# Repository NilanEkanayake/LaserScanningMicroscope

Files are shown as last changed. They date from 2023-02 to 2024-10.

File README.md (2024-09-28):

PCB and schematic for an STM32G431-based Laser Scanning Microscope v2

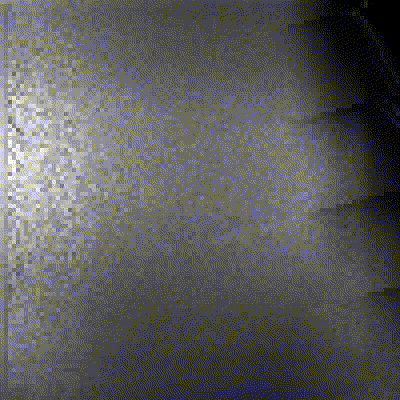
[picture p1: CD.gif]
A slow zoom in to a CD, gif
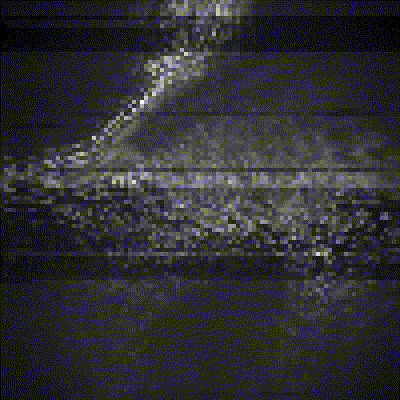
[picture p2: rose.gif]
A slow zoom in to a rose leaf, gif
  

The above GIFs show a slow zoom into a CD (all the way to the pits and lands), and a rose leaf, respectively. Both were taken with V1 of the microscope.

### Notes about V2 laser burnout and U5 overheating:
When V2 (likely V1 too) is powered on, the DAC/PWM pins are pulled high during the boot process. This cannot be fixed through software as far as I know.
The effect is that the laser driver circuit is given 3.3v on the DAC line briefly each time the PCB is plugged in. The current then provided to the laser is beyond what it can handle, and while it does not instantly burn out, it gets noticeably dimmer over time as the PCB is power-cycled. This effect is worsed by flashing firmware either with an STLink or through USB, as while in programming mode the pins are also pulled high. Therefore, make sure to disconnect the OPUs before flashing new firmware.

The solution I've found is to add a pull-down resistor to the laser DAC's output. I was able to hand-solder one, but a PCB fix will be required nonetheless as doing so is very finicky.

This issue also affects the VCMs as well. This results in a loose sample being thrown off the holder if one is present on power-on.

Also, U5 and the VCM/DAC_COARSE and VCM/DAC_Y resistors get uncomfortably hot during prolonged operation. This may be exacerbated by using heavier samples that increase the needed current to drive the bottom VCM.

For now, I recommend not directly using the project, and more as a source of inspiration. I am currently working on a new LSM version that fixes these issues (and others), but it will take a while.

-----------------------------------------------------------------

Uses two Optical Pickup Units (or OPU), model HOP-150x, one to hold the sample, the other to scan the sample with a laser. Each pickup covers one horizontal axis, while both use the Z axis to focus (bottom pickup for coarse focus, top one for fine focus)

Required parts (V2):

1x 3mm diameter metal rod, preferably 5cm. (I salvage mine from old CD/DVD players)

1x 26pin, 0.5mm pitch, 10cm length FFC with pins on the same side (for bottom OPU) (https://www.aliexpress.com/item/1005004140412156.html works for this and next part)

1x 26pin, 0.5mm pitch, 10cm length FFC with pins on the opposite side (for top OPU)

1x V2 PCB (I had mine entirely manufactured by JLCPCB - I chose as many of JLCPCB's "basic parts" as possible to reduce assembly cost)

1x 3D-printed enclosure (I printed mine using basic PLA on my own printer, but I assume you can also use JLCPCB's 3d-printing service for this too)

1x 3D-printed sample holder (WIP, not ready for prime time)

2x HOP-150x OPUs (I get mine from aliexpress)

Assembly (V2):
1. Remove the lens from the OPU destined to be the sample holder using a pair of tweezers, connect the FFC cable that has pins on the same side, and thread the cable through the slot in the enclosure, from the inside to the outside.
2. Gently push the OPU directly into the enclosure, making sure that the FFC cable doesn't snag.
3. Using a soldering iron, remove the large blob of solder on the edge of the large PCB on the top OPU, so that the pins are exposed and not shorted, and connect the FFC cable with pins on opposite sides
4. Slot the OPU lens-down into the protrusions sticking up from the enclosure, and slot the 3mm rod through the aligned OPU and enclosure on the side above the bottom OPU's FFC cable slot. The top OPU should now be able to swing upwards like a hinge for easy sample access.
5. Place the PCB into the slot on the side of the enclosure with the two FFC connectors facing up and right respectively, and connect the top OPU's cable to the connector on top of the PCB, and the bottom OPU's to the one on the right.
6. Swing the top OPU upwards and place the sample holder in the hole previously occupied by the lens on the bottom OPU. Samples are placed in the center of the holder.

To flash the PCB:

Method 1 (requires STLink, allows debugging):
1. Connect the PCB to a PC with USB and an STLink (Use the header's SWDIO, SWCLK and GND pins, pinout in the schematic).
2. Open LSM-scanner in STM32CubeIDE and flash it to the PCB.

Method 2 (no STLink required, but no debugging):
1. Install https://www.st.com/en/development-tools/stm32cubeprog.html
2. Open LSM-scanner in STM32CubeIDE, right-click the project in the left bar and select "Build Project".
3. Expand the "Binaries" tab under the project and right-click->copy the .elf file within, then paste it somewhere you'll remember in your filesystem
4. Open STM32CubeProgrammer and connect the PCB to a PC via USB while holding down the button above the USB-C port.
5. Click the little reload icon within "USB Configuration", and the PCB should show up as USB1.
6. Select the "Open File" tab and browse to the .elf file from before, then click "Download".
7. After the download is complete, unplug and replug the USB connection, without holding down the button (only needed when flashing with USB)

To install the required packages and load LSM-client, open a terminal in the LSM-client folder and run:
```
python3 -m pip install -r requirements.txt
```
Then to launch the software:
```
python3 LSMclient.py
```

NOTES:
1. FES signal in V2 is noisy, haven't figured out why yet, overall doesn't hugely affect results.
2. OPU sample holder is a WIP
3. V2 doesn't include the debug header pins in the BOM, as wires or pins can be manually soldered with very little effort and aren't necessary for most users.

Credit to https://github.com/kototoibashi/dvd-pickup-microscope-poc and https://github.com/GaudiLabs/OpenLaserScanningMicroscope for schematic ideas and OPU pinout

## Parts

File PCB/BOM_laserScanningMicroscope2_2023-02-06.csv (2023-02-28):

ID | Name | Designator | Footprint | Quantity | Manufacturer Part | Manufacturer | Supplier | Supplier Part | Price | JLCPCB Part Class
1 | 1uF | C1,C8 | C0402 | 2 | CL05A105KA5NQNC | SAMSUNG(三星) | LCSC | C52923 | 0.001 | Basic Part
2 | 100nF | C2,C4,C5,C6,C7,C9,C12 | C0402 | 7 | CL05B104KB54PNC | SAMSUNG(三星) | LCSC | C307331 | 0.001 | Basic Part
3 | 10uF | C3 | C0402 | 1 | CL05A106MQ5NUNC | SAMSUNG(三星) | LCSC | C15525 | 0.001 | Basic Part
4 | 15pF | C10,C13 | C0603 | 2 | CL10C150JB8NNNC | SAMSUNG(三星) | LCSC | C1644 | 0.001 | Basic Part
5 | 10uF | C11 | CAP-SMD_L3.2-W1.6-RD-C7171 | 1 | TAJA106K016RNJ | Kyocera AVX | LCSC | C7171 | 0.014 | Basic Part
6 | 22uF | C14,C15 | C0603 | 2 | CL10A226MQ8NRNC | SAMSUNG(三星) | LCSC | C59461 | 0.002 | Basic Part
7 | 10nF | C16 | C0603 | 1 | 0603B103K500NT | FH(风华) | LCSC | C57112 |  | Basic Part
8 | 100nF | C17 | C0603 | 1 | CC0603KRX7R9BB104 | YAGEO(国巨) | LCSC | C14663 |  | Basic Part
9 | XW05200-26 | FPC1,FPC2 | FPC-SMD_26P-P0.50_XW05200-26 | 2 | XW05200-26 | MINTRON(明硕) | LCSC | C376067 | 0.045 | Extended Part
10 | 12251215CNG0S115001 | H1 | HDR-TH_30P-P2.54-V-M-R2-C15-S2.54 | 1 | 12251215CNG0S115001 | JILN(锦凌) | LCSC | C429951 | 0.015 | Extended Part
11 | BLM18RK102SN1D | L1 | L0603 | 1 | BLM18RK102SN1D | muRata(村田) | LCSC | C88986 | 0.003 | Extended Part
12 | 220Ω | L3 | L0603 | 1 | BLM18PG221SN1D | muRata(村田) | LCSC | C80165 | 0.001 | Extended Part
13 | 0805G (Green) | LED2 | LED0805-RD_GREEN | 1 | KT-0805翠绿 (SMT业务专用) | null | LCSC | C2297 |  | Basic Part
14 | 1.2kΩ | R1,R2 | R0603 | 2 | 0603WAF1201T5E | UNI-ROYAL(厚声) | LCSC | C22765 |  | Basic Part
15 | 30kΩ | R3,R4 | R0603 | 2 | 0603WAF3002T5E | UNI-ROYAL(厚声) | LCSC | C22984 |  | Basic Part
16 | 7.5kΩ | R5 | R0603 | 1 | 0603WAF7501T5E | UNI-ROYAL(厚声) | LCSC | C23234 |  | Basic Part
17 | 4.3kΩ | R6 | R0603 | 1 | 0603WAF4301T5E | UNI-ROYAL(厚声) | LCSC | C23159 |  | Basic Part
18 | 10kΩ | R7 | R0603 | 1 | 0603WAF1002T5E | UNI-ROYAL(厚声) | LCSC | C25804 |  | Basic Part
19 | 4.7Ω | R8 | R0603 | 1 | 0603WAF470KT5E | UNI-ROYAL(厚声) | LCSC | C23164 |  | Basic Part
20 | 62kΩ | R9,R16 | R0603 | 2 | 0603WAF6202T5E | UNI-ROYAL(厚声) | LCSC | C23221 |  | Basic Part
21 | 20kΩ | R10,R11,R12,R14,R15,R18,R20,R21 | R0603 | 8 | 0603WAF2002T5E | UNI-ROYAL(厚声) | LCSC | C4184 |  | Basic Part
22 | 33Ω | R13 | R0603 | 1 | 0603WAF330JT5E | UNI-ROYAL(厚声) | LCSC | C23140 |  | Basic Part
23 | 56kΩ | R17 | R0603 | 1 | 0603WAF5602T5E | UNI-ROYAL(厚声) | LCSC | C23206 |  | Basic Part
24 | 200kΩ | R19 | R0603 | 1 | 0603WAF2003T5E | UNI-ROYAL(厚声) | LCSC | C25811 |  | Basic Part
25 | 330Ω | R23 | R0402 | 1 | 0402WGF3300TCE | UNI-ROYAL(厚声) | LCSC | C25104 |  | Basic Part
26 | 300Ω | R30 | R0603 | 1 | 0603WAF3000T5E | UNI-ROYAL(厚声) | LCSC | C23025 |  | Basic Part
27 | SS-12D01-G040 | SW1,SW2 | SW-TH_SS-12D01-GX | 2 | SS-12D01-G040 | G-Switch(品赞) | LCSC | C2876014 | 0.013 | Extended Part
28 | RS324AXP | U1,U2,U6 | SOP-14_L8.6-W3.9-P1.27-LS6.0-BL | 3 | RS324AXP | RUNIC(润石) | LCSC | C2887731 | 0.029 | Extended Part
29 | STM32G473CBT6 | U3 | LQFP-48_L7.0-W7.0-P0.50-LS9.0-BL | 1 | STM32G473CBT6 | ST(意法半导体) | LCSC | C730111 | 0.799 | Extended Part
30 | AMS1117-3.3 | U5 | SOT-223-3_L6.5-W3.4-P2.30-LS7.0-BR | 1 | AMS1117-3.3 | AMS | LCSC | C6186 | 0.025 | Basic Part
31 | U254-051T-4BH23-F2S | USB1 | MICRO-USB-SMD_U254-051T-4BH23-F2S | 1 | U254-051T-4BH23-F2S | XKB Connectivity(中国星坤) | LCSC | C2682230 | 0.01 | Extended Part
32 | 25MHz | X1 | OSC-SMD_4P-L3.2-W2.5-BL | 1 | X322525MOB4SI | YXC(扬兴晶振) | LCSC | C9006 | 0.014 | Basic Part

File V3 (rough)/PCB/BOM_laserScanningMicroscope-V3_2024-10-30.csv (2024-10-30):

ID | Name | Designator | Footprint | Quantity | Manufacturer Part | Manufacturer | Supplier | Supplier Part | Price
1 | 100nF | C1,C2,C4,C5,C6,C7,C9,C23,C24,C26 | C0402 | 10 | CL05B104KB54PNC | SAMSUNG(三星) | LCSC | C307331 | 0.004
2 | 10uF | C3 | C0402 | 1 | CL05A106MQ5NUNC | SAMSUNG(三星) | LCSC | C15525 | 0.004
3 | 1uF | C8,C25 | C0402 | 2 | CL05A105KA5NQNC | SAMSUNG(三星) | LCSC | C52923 | 0.003
4 | 15pF | C10,C13 | C0402 | 2 | 0402CG150J500NT | FH(风华) | LCSC | C1548 | 0.001
5 | 100nF | C12 | C0402 | 1 | CL05B104KO5NNNC | SAMSUNG(三星) | LCSC | C1525 | 0.001
6 | 22pF | C18,C20,C21,C22 | C0402 | 4 | 0402CG220J500NT | FH(风华) | LCSC | C1555 | 0.001
7 | 1uF | C14,C15 | C0603 | 2 | CL10A105KB8NNNC | SAMSUNG(三星) | LCSC | C15849 | 0.004
8 | 10nF | C16 | C0603 | 1 | 0603B103K500NT | FH(风华) | LCSC | C57112 | 0.002
9 | 100nF | C17 | C0603 | 1 | CC0603KRX7R9BB104 | YAGEO(国巨) | LCSC | C14663 | 0.002
10 | 4.7uF | C28 | C0603 | 1 | CL10A475KO8NNNC | SAMSUNG(三星) | LCSC | C19666 | 0.009
11 | XW05202-260R-00 | FPC1,FPC2 | FPC-SMD_26P-P0.50_HCTL_XW05202-260R-00 | 2 | XW05202-260R-00 | HCTL(华灿天禄) | LCSC | C2906122 | 0.087
12 | 100Ω | L1 | L0805 | 1 | GZ2012D101TF | Sunlord(顺络) | LCSC | C1015 | 0.01
13 | 600Ω | L2 | L0805 | 1 | GZ2012D601TF | Sunlord(顺络) | LCSC | C1017 | 0.013
14 | YELLOW | LED1 | LED0603-RD-YELLOW | 1 | 19-213/Y2C-CQ2R2L/3T(CY) | EVERLIGHT(亿光) | LCSC | C72038 | 0.021
15 | 15Ω | R1 | R0603 | 1 | 0603WAF150JT5E | UNI-ROYAL(厚声) | LCSC | C22810 | 0.001
16 | 20Ω | R2 | R0603 | 1 | 0603WAF200JT5E | UNI-ROYAL(厚声) | LCSC | C22950 | 0.001
17 | 10kΩ | R7,R38,R39 | R0402 | 3 | 0402WGF1002TCE | UNI-ROYAL(厚声) | LCSC | C25744 | 0.001
18 | 20kΩ | R10,R19,R20,R27,R30,R32 | R0402 | 6 | 0402WGF2002TCE | UNI-ROYAL(厚声) | LCSC | C25765 | 0.001
19 | 39kΩ | R11,R17 | R0402 | 2 | 0402WGF3902TCE | UNI-ROYAL(厚声) | LCSC | C25783 | 0.001
20 | 120kΩ | R12,R16 | R0402 | 2 | 0402WGF1203TCE | UNI-ROYAL(厚声) | LCSC | C25750 | 0.001
21 | 56kΩ | R13 | R0402 | 1 | 0402WGF5602TCE | UNI-ROYAL(厚声) | LCSC | C25796 | 0.001
22 | 1kΩ | R22 | R0402 | 1 | 0402WGF1001TCE | UNI-ROYAL(厚声) | LCSC | C11702 | 0.001
23 | 330Ω | R23 | R0402 | 1 | 0402WGF3300TCE | UNI-ROYAL(厚声) | LCSC | C25104 | 0.001
24 | 5.1kΩ | R24,R25 | R0402 | 2 | 0402WGF5101TCE | UNI-ROYAL(厚声) | LCSC | C25905 | 0.001
25 | 200kΩ | R26 | R0402 | 1 | 0402WGF2003TCE | UNI-ROYAL(厚声) | LCSC | C25764 | 0.001
26 | 6.8kΩ | R36 | R0402 | 1 | 0402WGF6801TCE | UNI-ROYAL(厚声) | LCSC | C25917 | 0.001
27 | 12kΩ | R37 | R0402 | 1 | 0402WGF1202TCE | UNI-ROYAL(厚声) | LCSC | C25752 | 0.001
28 | 5.6kΩ | R18,R21,R29,R31 | R0402 | 4 | 0402WGF5601TCE | UNI-ROYAL(厚声) | LCSC | C25908 | 0.001
29 | TS-1187A-B-A-B | SW | SW-SMD_4P-L5.1-W5.1-P3.70-LS6.5-TL-2 | 1 | TS-1187A-B-A-B | XKB Connectivity(中国星坤) | LCSC | C318884 | 0.017
30 | RS324AXQ | U2,U3,U5 | TSSOP-14_L5.0-W4.4-P0.65-LS6.4-BL | 3 | RS324AXQ | RUNIC(润石) | LCSC | C2887733 | 0.172
31 | STM32G474RBT6 | U6 | LQFP-64_L10.0-W10.0-P0.50-LS12.0-BL | 1 | STM32G474RBT6 | ST(意法半导体) | LCSC | C529413 | 3.356
32 | XC6206P332MR | U7 | SOT-23-3_L2.9-W1.6-P1.90-LS2.8-BR | 1 | XC6206P332MR | TOREX(特瑞仕) | LCSC | C5446 | 0.098
33 | 25MHz | X1 | OSC-SMD_4P-L3.2-W2.5-BL | 1 | X322525MOB4SI | YXC(扬兴晶振) | LCSC | C9006 | 0.06
34 | 2.2Ω | R3,R4,R5,R6 | R0603 | 4 | 0603WAF220KT5E | UNI-ROYAL(厚声) | LCSC | C22939 | 0.001
35 | X1311WV-03J-C18D27 | U1 | HDR-TH_3P-P1.27-V-M | 1 | X1311WV-03J-C18D27 | XKB Connectivity(中国星坤) | LCSC | C2881648 | 0.049
36 | TYPE-C 16PIN 2MD(073) | USB | USB-C-SMD_TYPE-C-6PIN-2MD-073 | 1 | TYPE-C 16PIN 2MD(073) | SHOU HAN(首韩) | LCSC | C2765186 | 0.054

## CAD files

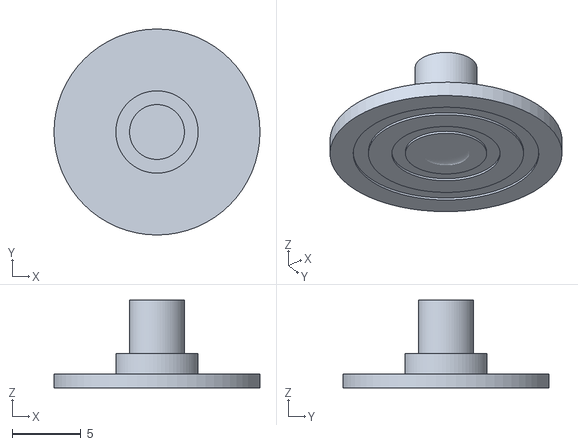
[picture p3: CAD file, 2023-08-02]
Enclosure-and-holder-STLs/sample_holder.stl
15.0 x 15.0 x 6.40

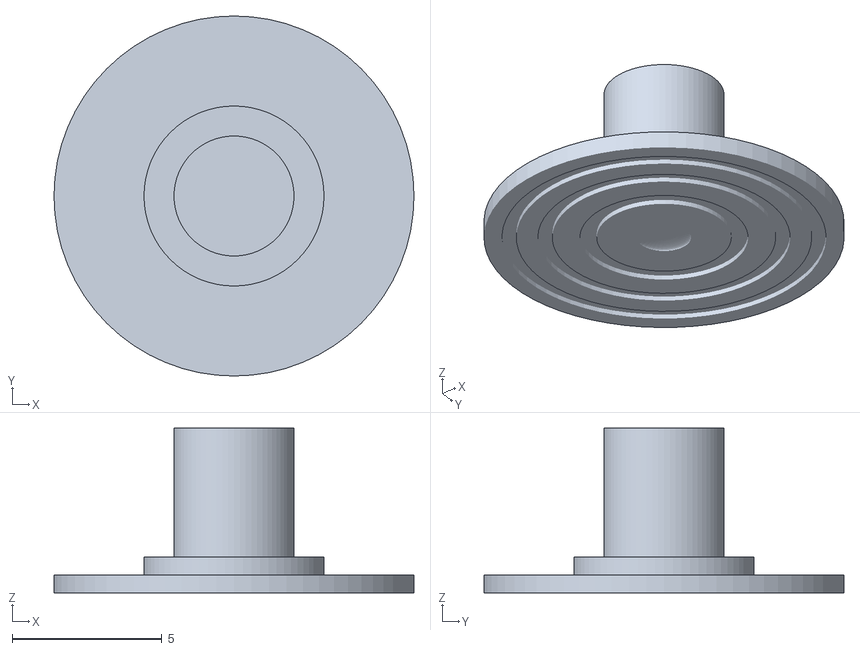
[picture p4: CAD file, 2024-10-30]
V3 (rough)/optional_thinner_sample_holder.stl
12.0 x 12.0 x 5.50

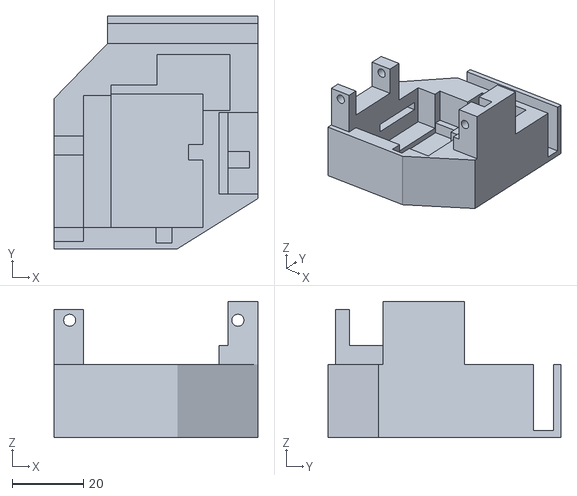
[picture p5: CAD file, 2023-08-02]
Enclosure-and-holder-STLs/enclosure.stl
57.2 x 65.2 x 38.2

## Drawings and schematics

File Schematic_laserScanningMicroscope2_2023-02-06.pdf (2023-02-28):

## Focus VCM and Laser Driver

## BOOT0 switch

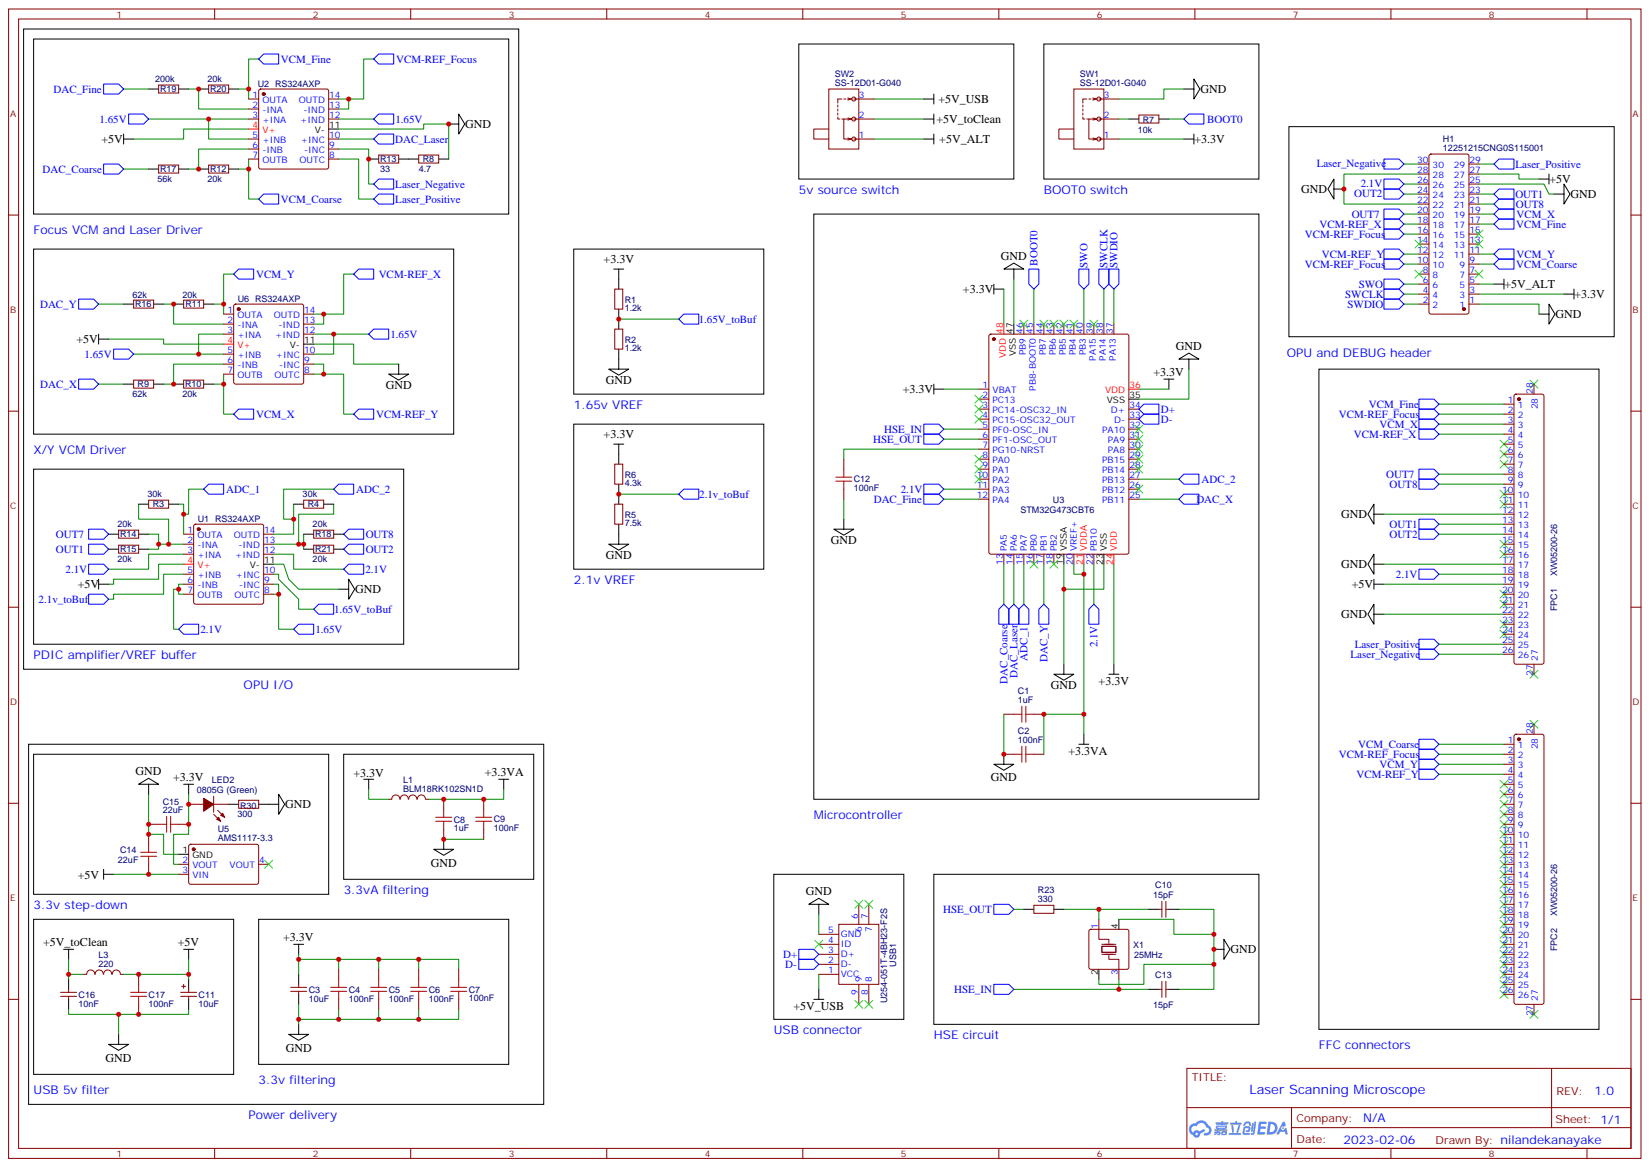
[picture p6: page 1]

+INC 10 V- 11 +IND 12 -IND 13 OUTD 14

OPU and DEBUG header

PDIC amplifier/VREF buffer

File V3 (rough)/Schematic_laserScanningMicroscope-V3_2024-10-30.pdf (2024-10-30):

## Top OPU driver

## 1.65v VREF

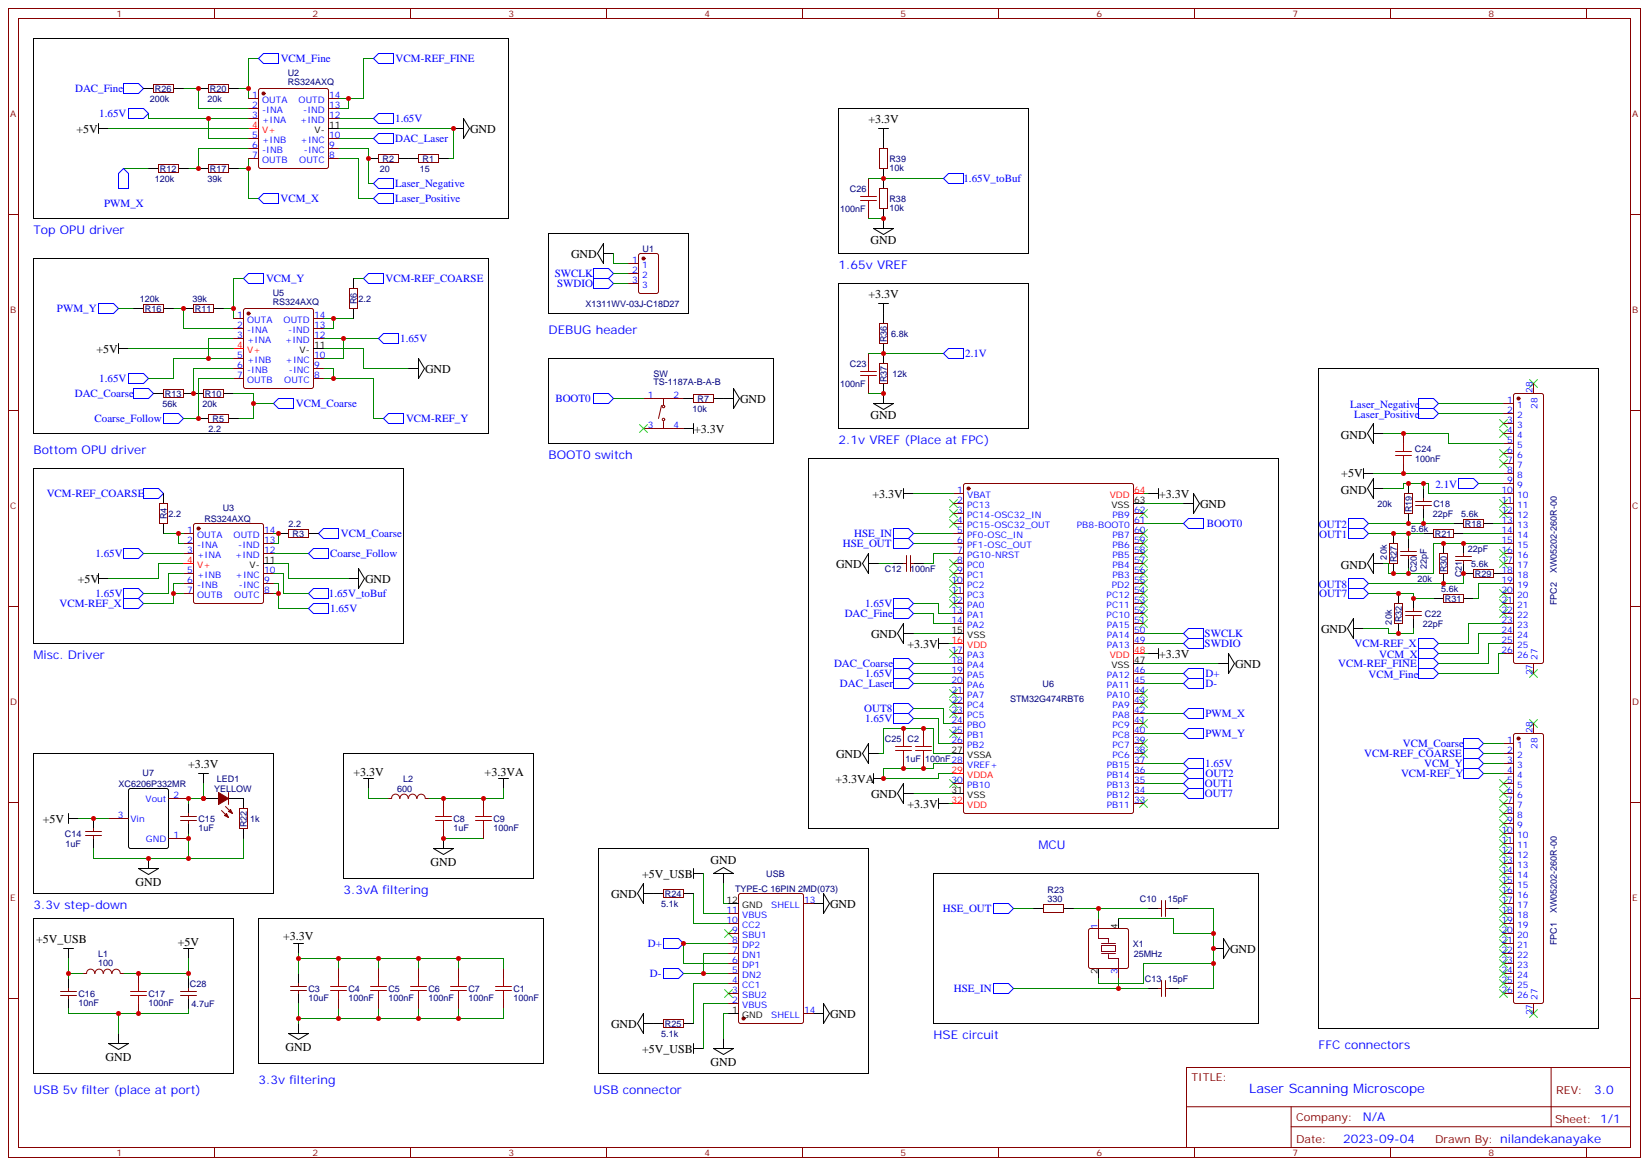
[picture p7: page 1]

GND
2.1v VREF (Place at FPC)

+INC 10 V- 11 +IND 12 -IND 13 OUTD 14

USB 5v filter (place at port)

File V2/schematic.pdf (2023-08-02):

## Top OPU driver

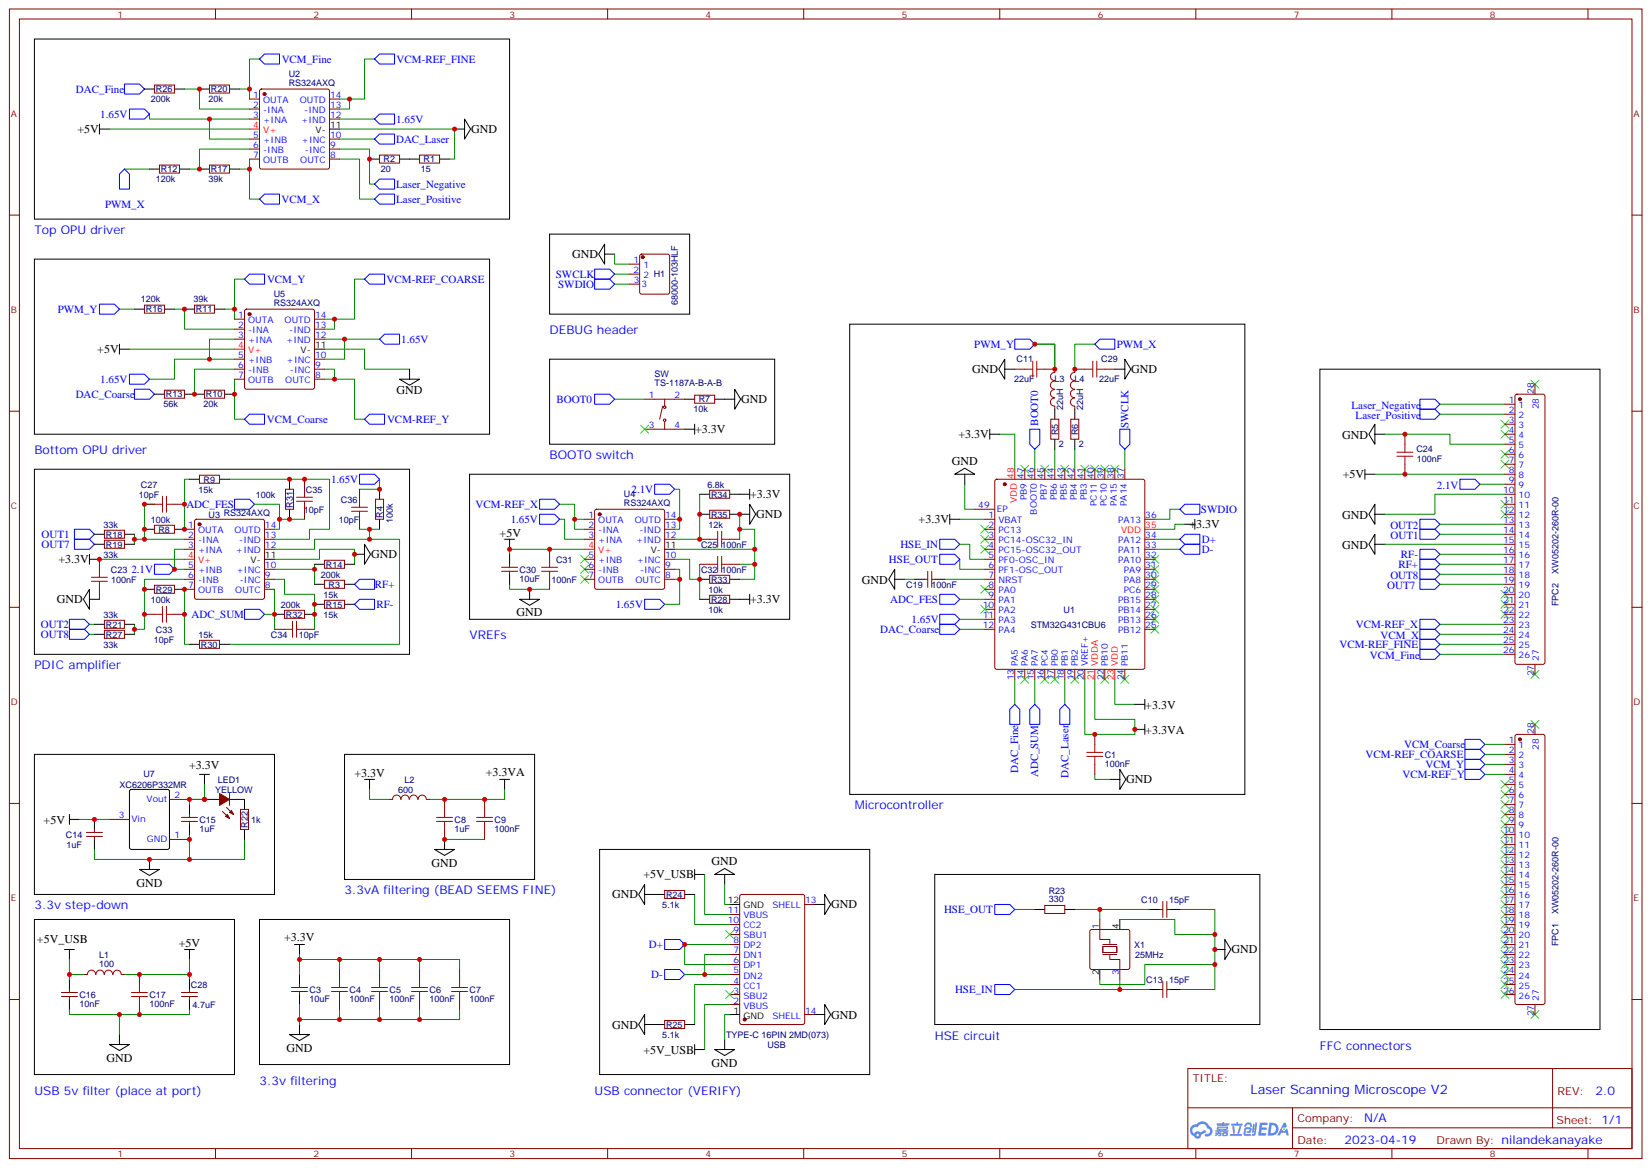
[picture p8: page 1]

+INC 10 V- 11 +IND 12 -IND 13 OUTD 14

3.3vA filtering (BEAD SEEMS FINE)

USB 5v filter (place at port)

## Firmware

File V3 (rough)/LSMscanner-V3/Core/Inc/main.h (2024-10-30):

/* USER CODE BEGIN Header */
/**
  ******************************************************************************
  * @file           : main.h
  * @brief          : Header for main.c file.
  *                   This file contains the common defines of the application.
  ******************************************************************************
  * @attention
  *
  * Copyright (c) 2023 STMicroelectronics.
  * All rights reserved.
  *
  * This software is licensed under terms that can be found in the LICENSE file
  * in the root directory of this software component.
  * If no LICENSE file comes with this software, it is provided AS-IS.
  *
  ******************************************************************************
  */
/* USER CODE END Header */

/* Define to prevent recursive inclusion -------------------------------------*/
#ifndef __MAIN_H
#define __MAIN_H

#ifdef __cplusplus
extern "C" {
#endif

/* Includes ------------------------------------------------------------------*/
#include "stm32g4xx_hal.h"

/* Private includes ----------------------------------------------------------*/
/* USER CODE BEGIN Includes */

/* USER CODE END Includes */

/* Exported types ------------------------------------------------------------*/
/* USER CODE BEGIN ET */

/* USER CODE END ET */

/* Exported constants --------------------------------------------------------*/
/* USER CODE BEGIN EC */

/* USER CODE END EC */

/* Exported macro ------------------------------------------------------------*/
/* USER CODE BEGIN EM */

/* USER CODE END EM */

void HAL_HRTIM_MspPostInit(HRTIM_HandleTypeDef *hhrtim);

/* Exported functions prototypes ---------------------------------------------*/
void Error_Handler(void);

/* USER CODE BEGIN EFP */

/* USER CODE END EFP */

/* Private defines -----------------------------------------------------------*/
#define ADC3_BIAS_Pin GPIO_PIN_1
#define ADC3_BIAS_GPIO_Port GPIOA
#define DAC_FINE_Pin GPIO_PIN_2
#define DAC_FINE_GPIO_Port GPIOA
#define DAC_Coarse_Pin GPIO_PIN_4
#define DAC_Coarse_GPIO_Port GPIOA
#define ADC4_BIAS_Pin GPIO_PIN_5
#define ADC4_BIAS_GPIO_Port GPIOA
#define DAC_Laser_Pin GPIO_PIN_6
#define DAC_Laser_GPIO_Port GPIOA
#define ADC4_IN_Pin GPIO_PIN_0
#define ADC4_IN_GPIO_Port GPIOB
#define ADC1_BIAS_Pin GPIO_PIN_2
#define ADC1_BIAS_GPIO_Port GPIOB
#define ADC3_IN_Pin GPIO_PIN_12
#define ADC3_IN_GPIO_Port GPIOB
#define ADC1_IN_Pin GPIO_PIN_13
#define ADC1_IN_GPIO_Port GPIOB
#define ADC2_IN_Pin GPIO_PIN_14
#define ADC2_IN_GPIO_Port GPIOB
#define PWM_Y_Pin GPIO_PIN_8
#define PWM_Y_GPIO_Port GPIOC
#define PWM_X_Pin GPIO_PIN_8
#define PWM_X_GPIO_Port GPIOA
#define SWDIO_Pin GPIO_PIN_13
#define SWDIO_GPIO_Port GPIOA
#define SWCLK_Pin GPIO_PIN_14
#define SWCLK_GPIO_Port GPIOA

/* USER CODE BEGIN Private defines */

/* USER CODE END Private defines */

#ifdef __cplusplus
}
#endif

#endif /* __MAIN_H */

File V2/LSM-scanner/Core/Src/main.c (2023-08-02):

/* USER CODE BEGIN Header */
/**
  ******************************************************************************
  * @file           : main.c
  * @brief          : Main program body
  ******************************************************************************
  * @attention
  *
  * Copyright (c) 2023 STMicroelectronics.
  * All rights reserved.
  *
  * This software is licensed under terms that can be found in the LICENSE file
  * in the root directory of this software component.
  * If no LICENSE file comes with this software, it is provided AS-IS.
  *
  ******************************************************************************
  */
/* USER CODE END Header */
/* Includes ------------------------------------------------------------------*/
#include "main.h"
#include "usb_device.h"

/* Private includes ----------------------------------------------------------*/
/* USER CODE BEGIN Includes */
#include <string.h>
#include <stdbool.h>
#include <math.h>
#include <ctype.h>
#include "usbd_cdc_if.h"
#include<stdio.h>
#include<stdlib.h>
/* USER CODE END Includes */

/* Private typedef -----------------------------------------------------------*/
/* USER CODE BEGIN PTD */

/* USER CODE END PTD */

/* Private define ------------------------------------------------------------*/
/* USER CODE BEGIN PD */

/* USER CODE END PD */

/* Private macro -------------------------------------------------------------*/
/* USER CODE BEGIN PM */

/* USER CODE END PM */

/* Private variables ---------------------------------------------------------*/
ADC_HandleTypeDef hadc1;
ADC_HandleTypeDef hadc2;

DAC_HandleTypeDef hdac1;
DAC_HandleTypeDef hdac3;

OPAMP_HandleTypeDef hopamp1;
OPAMP_HandleTypeDef hopamp2;
OPAMP_HandleTypeDef hopamp3;

TIM_HandleTypeDef htim1;
TIM_HandleTypeDef htim3;
TIM_HandleTypeDef htim4;

/* USER CODE BEGIN PV */
//1 -> int between 1 and 8191
uint16_t xRes = 200;
//2 -> int between 1 and 8191
uint16_t yRes = 200;
//3 -> int between 1 and 8191
uint16_t skipSteps = 1;

//4 -> int between 0 and 8191
uint16_t xOffset = 4095;
//5 -> int between 0 and 8191
uint16_t yOffset = 4095;
//8 -> int between 1 and 20
uint8_t adcAvg = 8;

//7 -> int between 0 and 2500
uint16_t laserPower = 2200;

//image data buffer -> set a little under the USB CDC 512 limit
static const uint16_t lenBuffer = 500;
static unsigned char imageData[500]; //apparently can't use lenBuffer

int pgaGain = OPAMP_PGA_GAIN_2_OR_MINUS_1;

int scanOffsetX = 0;
int scanOffsetY = 0;
/* USER CODE END PV */

/* Private function prototypes -----------------------------------------------*/
void SystemClock_Config(void);
static void MX_GPIO_Init(void);
static void MX_DAC1_Init(void);
static void MX_DAC3_Init(void);
static void MX_OPAMP1_Init(void);
static void MX_OPAMP2_Init(void);
static void MX_OPAMP3_Init(void);
static void MX_TIM3_Init(void);
static void MX_TIM4_Init(void);
static void MX_TIM1_Init(void);
static void MX_ADC1_Init(void);
static void MX_ADC2_Init(void);
/* USER CODE BEGIN PFP */

/* USER CODE END PFP */

/* Private user code ---------------------------------------------------------*/
/* USER CODE BEGIN 0 */

//microsecond delay (not used)
void delay(uint32_t us) {
	//from AN4776 page 10, 1.3.1
	if (us > 65535) { //a check to see if the scans asks for bad delays
		printf("A delay of %d is too long!", us);
		us = 65535; //set to max
	}
	TIM1->ARR = us;
	TIM1->CNT = 0;
	TIM1->CR1 |= TIM_CR1_CEN; //enable timer
	while (TIM1->CNT < us)
		; //wait
	TIM1->CR1 &= ~TIM_CR1_CEN; //disable timer
}

//USB cdc transmit
//https://github.com/alexeykosinov/Redirect-printf-to-USB-VCP-on-STM32H7-MCU
int _write(int file, char *ptr, int len) {
	static uint8_t rc = USBD_OK;

	do {
		rc = CDC_Transmit_FS((unsigned char*) ptr, len);
	} while (USBD_BUSY == rc);

	if (USBD_FAIL == rc) {
		/// NOTE: Should never reach here.
		/// TODO: Handle this error.
		return 0;
	}
	return len;
}

//USB cdc receive
uint8_t buffer[64];
bool newReceived;

//ADC
uint32_t analogRead(uint8_t channel) {
	uint32_t ADCValue = 0;
	if (channel == 0) { //SUM
		HAL_ADC_Start(&hadc2);
		if (HAL_ADC_PollForConversion(&hadc2, 1000000) == HAL_OK) {
			ADCValue = 65520-HAL_ADC_GetValue(&hadc2); //4095*8
		}
		HAL_ADC_Stop(&hadc2);
	} else if (channel == 1) { //FES
		HAL_ADC_Start(&hadc1);
		if (HAL_ADC_PollForConversion(&hadc1, 1000000) == HAL_OK) {
			ADCValue = HAL_ADC_GetValue(&hadc1);
		}
		HAL_ADC_Stop(&hadc1);
	}
	return ADCValue/16; //divide by 8 for 8x oversampling
}

//parse usb serial input
uint16_t getNum() {
	uint16_t num = 0;
	for (int i = 1; i <= 4; i++) {
		if (isdigit(buffer[i])) { //only works if buffer isn't initialized with all zeros - shouldn't be
			num *= 10;
			num += buffer[i] - '0';
		}
	}
	return num;
}

//fine focus
void fineFocus() {
	int32_t currentAdc;
	int16_t topAdc = -10000;
	int16_t bottomAdc = 10000;
	int16_t topDac = 0;
	int16_t bottomDac = 0;
	int16_t middleDac;
	int8_t precision = 2; //normally 7 for 13-bit

	//set offsets
	htim3.Instance->CCR1 = xOffset;
	htim4.Instance->CCR1 = yOffset;

	//set laser power
	DAC3->DHR12R2 = laserPower;

	//reset fine focus
	DAC1->DHR12R2 = 0;

	//delay to settle
	HAL_Delay(100);

	for (int i = 0; i < 4096; i += precision) { //can do +=5?
		DAC1->DHR12R2 = i;
		//delay_us(1000);
		HAL_Delay(8);
		currentAdc = analogRead(1);
		if (currentAdc > topAdc) {
			topAdc = currentAdc;
			topDac = i;
			HAL_Delay(40);
		} else if (currentAdc < bottomAdc) {
			bottomAdc = currentAdc;
			bottomDac = i;
			HAL_Delay(40);
		}
		delay(6000);
		printf("%d,%d\r\n", i, currentAdc); //print to see curve
	}
	printf("Done\r\n");
	middleDac = ((topDac - bottomDac) / 2) + bottomDac;

	//temp offset
	middleDac += 40;

	for (int i = 0; i <= middleDac; i += precision) {
		DAC1->DHR12R2 = i;
		if (i <= 2) { //don't need large timer if not resetting axis
			HAL_Delay(200);
		} else {
			delay(2000);
		}
		currentAdc = analogRead(1);
		printf("%d,%d\r\n", i, currentAdc);
		delay(1000);
	}



	HAL_Delay(300);
	printf("Done\r\n");
}

//coarse focus
void coarseFocus() {
	uint32_t sum = 0;
	uint16_t minDac = 0;
	uint8_t precision = 1;
	uint16_t minSum = 10000;

	//set offsets
	htim3.Instance->CCR1 = xOffset;
	htim4.Instance->CCR1 = yOffset;


	//set fine focus to close-to-center to avoid center instability and coarse to start
	DAC1->DHR12R2 = 2300;

	//reset coarse focus
	DAC1->DHR12R1 = 0;

	//set laser power
	DAC3->DHR12R2 = laserPower;

	//delay to settle
	HAL_Delay(100);

	for (int i = 0; i < 4096; i += precision) {
		DAC1->DHR12R1 = i;
		delay(1000);
		sum = analogRead(0);
		if (sum < minSum) { //values get smaller as light increases (inverted)
			minSum = sum;
			minDac = i;
		}
		delay(1000);
		printf("%d,%d\r\n", i, sum); //print to see curve
	}
	printf("Done\r\n");

	// wind back to avoid dislodging sample
	for (int i = 4095; i >= 0; i -= precision) {
		DAC1->DHR12R1 = i;
		delay(200);
	}

	delay(2000);
	for (int i = 0; i <= minDac; i += precision) {
		DAC1->DHR12R1 = i;
		delay(1000);
		sum = analogRead(0);
		printf("%d,%d\r\n", i, sum);
		delay(1000);
	}

	HAL_Delay(300);
	printf("Done\r\n");
}

void fastScan() {

	int raw;

	DAC3->DHR12R2 = laserPower;

	//set offsets
	htim3.Instance->CCR1 = xOffset;
	htim4.Instance->CCR1 = yOffset;


	for (int y = 0; y < yRes; y++) {

		if (y == 0) {
			htim4.Instance->CCR1 = (scanOffsetY + (yRes*skipSteps)/2.55);
			delay(8197); //half of 61hz, resonance frequency of SF-HD65
		}

		htim4.Instance->CCR1 = (scanOffsetY + (y * skipSteps));

		for (int x = 0; x < xRes; x++) {
			raw = 0;

			//ringing compensation
			if (x == 0) {
				htim3.Instance->CCR1 = (scanOffsetX + (xRes*skipSteps)/2.35);
				delay(8197); //half of 61hz, resonance frequency of SF-HD65
			}

			htim3.Instance->CCR1 = (scanOffsetX + (x * skipSteps));

			raw = 8191 - analogRead(0);
			//delay(adcAvg*20);

			if (x + 1 == xRes) {
				printf("%d\r\n", raw);
			} else {
				printf("%d,", raw);
			}
		}

		//add delay later
	}
	printf("%d\r\n", 0);
}
/* USER CODE END 0 */

/**
  * @brief  The application entry point.
  * @retval int
  */
int main(void)
{
  /* USER CODE BEGIN 1 */

  /* USER CODE END 1 */

  /* MCU Configuration--------------------------------------------------------*/

  /* Reset of all peripherals, Initializes the Flash interface and the Systick. */
  HAL_Init();

  /* USER CODE BEGIN Init */

  /* USER CODE END Init */

  /* Configure the system clock */
  SystemClock_Config();

  /* USER CODE BEGIN SysInit */

  /* USER CODE END SysInit */

  /* Initialize all configured peripherals */
  MX_GPIO_Init();
  MX_DAC1_Init();
  MX_DAC3_Init();
  MX_OPAMP1_Init();
  MX_OPAMP2_Init();
  MX_OPAMP3_Init();
  MX_TIM3_Init();
  MX_TIM4_Init();
  MX_TIM1_Init();
  MX_ADC1_Init();
  MX_ADC2_Init();
  MX_USB_Device_Init();
  /* USER CODE BEGIN 2 */
  //DAC SETUP
  HAL_DAC_Start(&hdac1, DAC_CHANNEL_1);
  HAL_DAC_Start(&hdac1, DAC_CHANNEL_2);
  HAL_DAC_Start(&hdac3, DAC_CHANNEL_2);

  //ADC SETUP
  HAL_ADCEx_Calibration_Start(&hadc1, ADC_SINGLE_ENDED);
  HAL_ADCEx_Calibration_Start(&hadc2, ADC_SINGLE_ENDED);

  //OP-AMP SETUP
  HAL_OPAMP_Start(&hopamp1);
  HAL_OPAMP_Start(&hopamp2);
  HAL_OPAMP_Start(&hopamp3);

  //DELAY TIMER SETUP
  HAL_TIM_Base_Start(&htim1);

  //PWM SETUP
  HAL_TIM_Base_Start(&htim3);
  HAL_TIM_PWM_Init(&htim3);
  HAL_TIM_Base_Start(&htim4);
  HAL_TIM_PWM_Init(&htim4);

  HAL_TIM_PWM_Start(&htim3, TIM_CHANNEL_1); //x
  HAL_TIM_PWM_Start(&htim4, TIM_CHANNEL_1); //y
  /* USER CODE END 2 */

  /* Infinite loop */
  /* USER CODE BEGIN WHILE */
  while (1)
  {
    /* USER CODE END WHILE */

    /* USER CODE BEGIN 3 */
	DAC3->DHR12R2 = 0;

	uint8_t adcGain = 1; //not sure I need this

	//buffer[0]
	uint8_t start;

	//value of following data after buffer[0]
	uint16_t num = 0;

	if (newReceived) {
		if (buffer[0] == '0') {
			start = 0;
		} else {
			start = buffer[0] - '0';
		}
		num = getNum();
		switch (start) {
		case 0:
			scanOffsetX = xOffset - (xRes * skipSteps / 2); // set focus to center of scanned image (make sure > 0)
			scanOffsetY = yOffset - (yRes * skipSteps / 2);

			if ((scanOffsetX + (xRes * skipSteps)) < 4096 && (scanOffsetX + (xRes * skipSteps)) >= 0) {
				if ((scanOffsetY + (yRes * skipSteps)) < 4096 && (scanOffsetY + (yRes * skipSteps)) >= 0) {
					if (num == 1) {
						fastScan();
						HAL_Delay(1);
					}
				} else {
					printf("X offset, res or skipSteps too high!\r\n");
				}
			} else {
				printf("Y offset, res or skipSteps too high!\r\n");
			}
			break;
		case 1:
			if (num < 8192 && num > 0) {
				xRes = num;
			}
			break;
		case 2:
			if (num < 8192 && num > 0) {
				yRes = num;
			}
			break;
		case 3:
			if (num < 8192 && num > 0) {
				skipSteps = num;
			}
			break;
		case 4:
			if (num < 8192) {
				xOffset = num;
			}
			break;
		case 5:
			if (num < 8192) {
				yOffset = num;
			}
			break;
		case 6:
			if (num <= 5) {
				//NOTE: V2.1 only has PGA gain for FES, not SUM
				adcGain = num;
				HAL_OPAMP_Stop(&hopamp1);
				switch (adcGain) {
				case 0:
					hopamp1.Init.PgaGain = OPAMP_PGA_GAIN_2_OR_MINUS_1;
					break;
				case 1:
					hopamp1.Init.PgaGain = OPAMP_PGA_GAIN_4_OR_MINUS_3;
					break;
				case 2:
					hopamp1.Init.PgaGain = OPAMP_PGA_GAIN_8_OR_MINUS_7;
					break;
				case 3:
					hopamp1.Init.PgaGain = OPAMP_PGA_GAIN_16_OR_MINUS_15;
					break;
				case 4:
					hopamp1.Init.PgaGain = OPAMP_PGA_GAIN_32_OR_MINUS_31;
					break;
				case 5:
					hopamp1.Init.PgaGain = OPAMP_PGA_GAIN_64_OR_MINUS_63;
					break;
				}
				HAL_Delay(2);
				if (HAL_OPAMP_Init(&hopamp1) != HAL_OK)
				{
					Error_Handler();
				}
				HAL_Delay(2);
				HAL_OPAMP_Start(&hopamp1);
			}
			break;
		case 7:
			if (num <= 3000) {
				laserPower = num;
			}
			break;
		case 8:
			if (num <= 20 && num != 0) {
				adcAvg = num;
			}
			break;
		case 9:
			if (num == 1) {
				fineFocus();
			} else if (num == 2) {
				coarseFocus();
			} else {
				printf("Bad input\r\n");
			}
			break;
		}
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

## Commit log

2023-02-28 Add primary files
    [BOM_laserScanningMicroscope2_2023-02-06.csv, PickAndPlace_PCB_laserScanningMicroscope_2023-02-06.csv]
2023-02-28 final oops
    [PickAndPlace_PCB_laserScanningMicroscope_2023-02-06.csv]
2023-02-28 Add files with better organization
    [BOM_laserScanningMicroscope2_2023-02-06.csv, PickAndPlace_PCB_laserScanningMicroscope_2023-02-06.csv]
2023-03-01 add picture of PCB
2023-08-02 Added preliminary V2
    [BOM_PCB_laserScanningMicroscope-V2_2023-08-02.csv, BOM_laserScanningMicroscope2_2023-02-06.csv, PickAndPlace_PCB_laserScanningMicroscope-V2_2023-08-02.csv, Pic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]
2024-08-11 Add laser burn-out notice
2024-09-28 include other affected resistors (or just issue from proximity, haven't got a thermal camera)
2024-10-30 added rough V3, still has issues
    [BOM_laserScanningMicroscope-V3_2024-10-30.csv, PickAndPlace_PCB_laserScanningMicroscope-V3_2024-10-30.csv]
2024-10-30 added thinner sample holder stl
    [optional_thinner_sample_holder.stl]
